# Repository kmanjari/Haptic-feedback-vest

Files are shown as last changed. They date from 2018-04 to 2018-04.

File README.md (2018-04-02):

# Haptic Feedback Vest for Obstacle Detection

Visit our instructable at http://www.instructables.com/id/Haptic-Feedback-Vest-for-Obstacle-Detection/ to view a description of the system breakdown!

This design utilizes a stereo camera and software (Python and SimpleCV) that parses the user's surroundings into a depth map using a Raspberry Pi platform. This depth map is then used to vibrate the vest at a particular location to signify an obstacle in that location. For example, a vibration in the upper left region of the vest would indicate a hazard in the upper-body/leftward side of the surroundings. We also developed a PCB and integrated the physical piezoelectric hardware into a vest to create a functional and wearable prototype.

Final project for EE285: Embedded Systems Workshop course at Stanford University.

Contributors: Shalini Ranmuthu, Vikram Prasad, Jacqueline Speiser, Steven Lin, Meredith Burkle

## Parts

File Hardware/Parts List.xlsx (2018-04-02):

Part | QTY | Cost Per Unit | Total Cost | Vendor | Link
Shorting Jumper | 10 | 0.77 | 0.77 | Digikey | http://www.digikey.com/product-detail/en/sullins-connector-solutions/SPC02SYAN/S9001-ND/76375
Heat Shrink Tubing 1/16" | 1 | 1.15 | 1.15 | Digikey | http://www.digikey.com/product-detail/en/alpha-wire/F221B1-16-BK100/A116B-4-ND/281667
Heat Shrink Tubing 3/32" | 1 | 1.22 | 1.22 | Digikey | http://www.digikey.com/product-detail/en/alpha-wire/F221B3-32-BK100/A332B-4-ND/281669
Fanny Pack | 1 | $15.99 | 15.99 | Amazon | https://www.amazon.com/SoJourner-Bags-Outer-Galaxy-Festival/dp/B01G4A9H9E
Adafruit Vibration Motor | 15 | 1.95 | 29.25 | Digikey | http://www.digikey.com/product-detail/en/adafruit-industries-llc/1201/1528-1177-ND/5353637
2n7002 Nmos | 30 | 0.131 | 3.93 | Digikey | http://www.digikey.com/product-detail/en/on-semiconductor/2N7002LT1G/2N7002LT1GOSCT-ND/917791
10K resistor(0805) | 50 | 0.0092 | 0.46 | Digikey | http://www.digikey.com/product-detail/en/stackpole-electronics-inc/RMCF0805JT10K0/RMCF0805JT10K0CT-ND/1942577
100nF capacitor (0805) | 10 | 0.037 | 0.37 | Digikey | http://www.digikey.com/product-detail/en/avx-corporation/08055C104KAT2A/478-1395-1-ND/564427
1K resistor (0805) | 10 | 0.018 | 0.18 | Digikey | http://www.digikey.com/product-detail/en/yageo/RC0805JR-071KL/311-1.0KARCT-ND/731165
PCA9685 (i2c->PWM controller) | 3 | 2.43 | 7.29 | Digkey | http://www.digikey.com/product-detail/en/nxp-semiconductors/PCA9685PW-Q900,118/568-5931-1-ND/2531218
Surface Mount Diode | 25 | 0.1084 | 2.71 | Digikey | http://www.digikey.com/product-detail/en/smc-diode-solutions/1N4148WTR/1655-1360-1-ND/6022805
Dual Breakaway Header | 3 | 0.93 | 2.79 | Digikey | http://www.digikey.com/product-detail/en/sullins-connector-solutions/PRPC020DAAN-RC/S2011EC-20-ND/2775274
1uF capacitor (TH, Electrolytic) | 3 | 0.11 | 0.33 | Digikey | http://www.digikey.com/product-detail/en/wurth-electronics-inc/860020672005/732-8851-1-ND/5728796
USB B receptacle | 2 | 0.5 | 1 | Digikey | http://www.digikey.com/product-detail/en/pulse-electronics-corporation/E8144-B02022-L/553-2272-ND/4868942
Connector (PCB to piezoelectrics) | 1 | 10.8 | 10.8 | Digikey | http://www.digikey.com/product-detail/en/3m/M1DXA-3440K/M1DXA-3440K-ND/46368
Battery Bank | 1 | $40.00 | 40 | Amazon | https://www.amazon.com/Anker-PowerCore-20100-Capacity-Technology/dp/B00X5RV14Y
GPIO Ribbon Cable | 1 | $2.95 | 2.95 | Adafruit | https://www.adafruit.com/product/1988
Logitech Webcam C310 | 2 | $29.99 | 59.98 | Amazon | https://www.amazon.com/Logitech-960-000585-HD-Webcam-C310/dp/B003LVZO8S?s=electronics
Raspberry Pi | 2 | $35 | $70 | MCM Electronics | http://www.mcmelectronics.com/product/83-17300?COM=superwidget-link_RaspberryPi+CMPNULL
Raspberry Pi Power Supply (for development) | 2 | $8.99 | $17.98 | MCM Electronics | http://www.mcmelectronics.com/product/28-21442
Micro SD cards | 2 | In-house | 0
Vest of wearer's choice |  |  |  | IKEA
USB-B to USB Cable

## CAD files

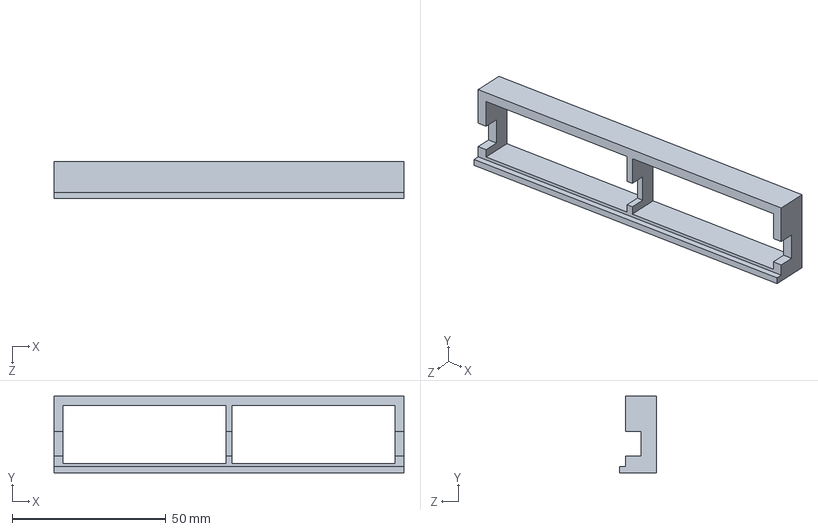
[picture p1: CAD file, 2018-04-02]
Hardware/Haptic Board V1 Gerbers/holder.SLDPRT
114.0 x 25.0 x 12.0 mm

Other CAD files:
Hardware/Haptic Board V1 Gerbers/holder.STL

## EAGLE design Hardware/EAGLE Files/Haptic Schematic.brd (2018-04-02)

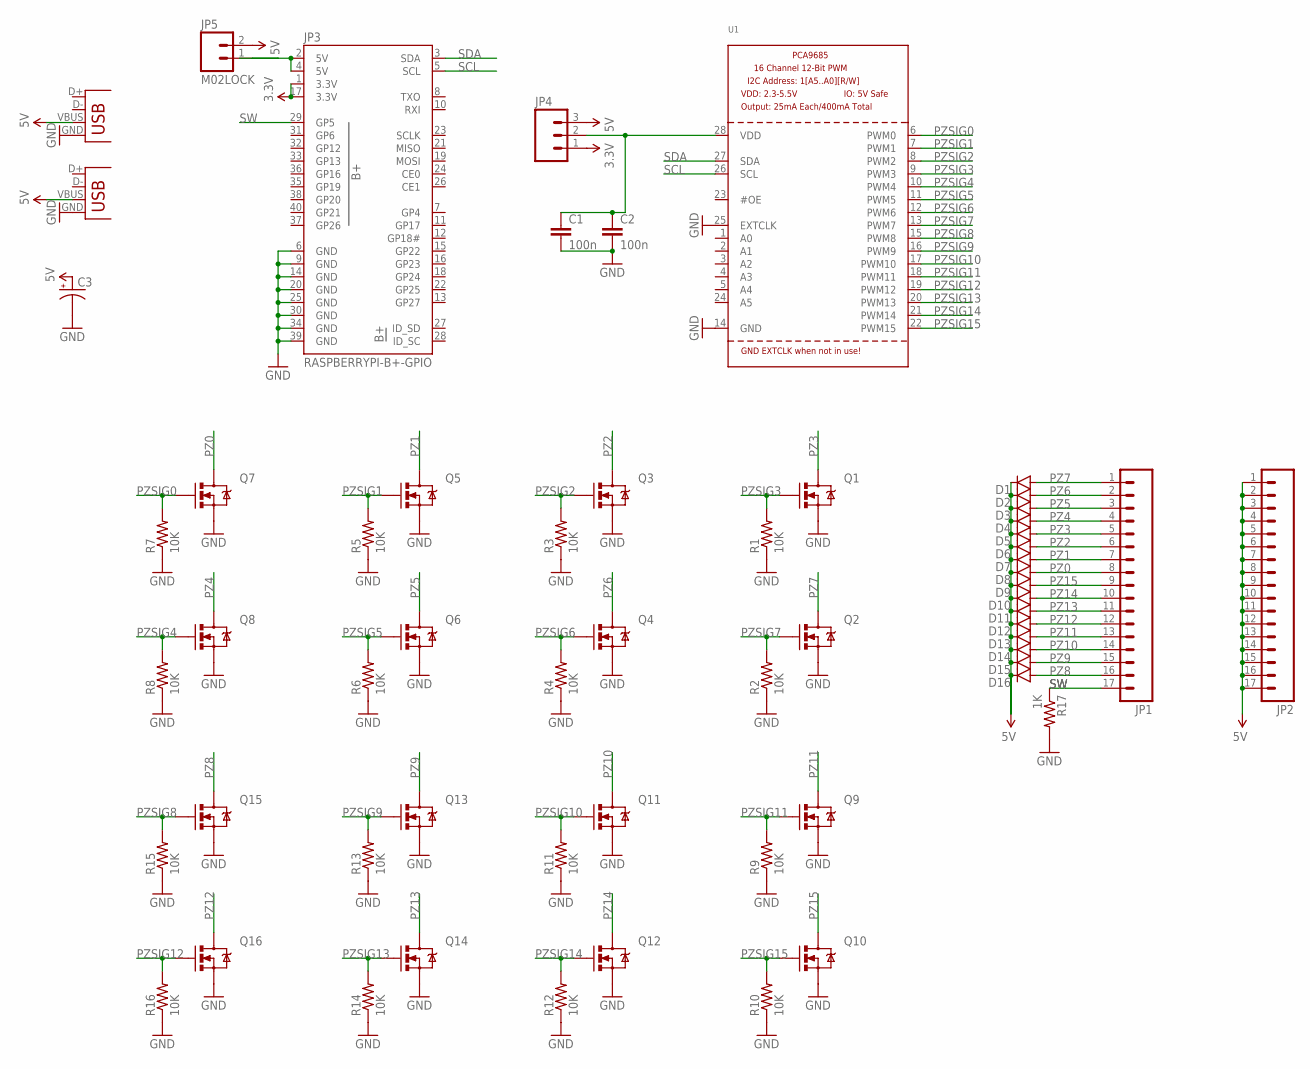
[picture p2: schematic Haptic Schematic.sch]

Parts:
C1, C2: 100n; 0805
C3: CAP_POLPTH2; CPOL-RADIAL-10UF-25V
D1, D2, D3, D4, D5, D6, D7, D8, D9, D10, D11, D12, D13, D14, D15, D16: DIODESOD523; SOD523
JP1, JP2: M17; 1X17
JP3: RASPBERRYPI-B+-GPIO; 2X20-SHROUDED
JP4: M03LOCK; 1X03_LOCK
JP5: M02LOCK; 1X02_LOCK
JP6, JP7: USB-B; USB-B-PTH
Q1, Q2, Q3, Q4, Q5, Q6, Q7, Q8, Q9, Q10, Q11, Q12, Q13, Q14, Q15, Q16: MOSFET-NCHANNEL2N7002PW; SOT323
R1, R2, R3, R4, R5, R6, R7, R8, R9, R10, R11, R12, R13, R14, R15, R16: 10K; 0805
R17: 1K; 0805
U1: PCA9685; TSSOP28

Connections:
3.3V: JP3.1 (3.3V), JP3.17 (3.3V), JP4.1
5V: C3.1 (+), D1.C, D2.C, D3.C, D4.C, D5.C, D6.C, D7.C, D8.C, D9.C, D10.C, D11.C, D12.C, D13.C, D14.C, D15.C, D16.C, JP2.1, JP2.2, JP2.3, JP2.4, JP2.5, JP2.6, JP2.7, JP2.8, JP2.9, JP2.10, JP2.11, JP2.12, JP2.13, JP2.14, JP2.15, JP2.16, JP2.17, JP4.3, JP5.2, JP6.VBUS, JP7.VBUS
GND: C1.2, C2.2, C3.2 (-), JP3.6 (GND), JP3.9 (GND), JP3.14 (GND), JP3.20 (GND), JP3.25 (GND), JP3.30 (GND), JP3.34 (GND), JP3.39 (GND), JP6.GND, JP7.GND, Q1.2 (S), Q2.2 (S), Q3.2 (S), Q4.2 (S), Q5.2 (S), Q6.2 (S), Q7.2 (S), Q8.2 (S), Q9.2 (S), Q10.2 (S), Q11.2 (S), Q12.2 (S), Q13.2 (S), Q14.2 (S), Q15.2 (S), Q16.2 (S), R1.1, R2.1, R3.1, R4.1, R5.1, R6.1, R7.1, R8.1, R9.1, R10.1, R11.1, R12.1, R13.1, R14.1, R15.1, R16.1, R17.2, U1.14 (GND), U1.25 (EXTCLK)
unnamed: JP3.2 (5V), JP3.4 (5V), JP5.1
unnamed: C1.1, C2.1, JP4.2, U1.28 (VDD)
PZ0: D8.A, JP1.8, Q7.3 (D)
PZ1: D7.A, JP1.7, Q5.3 (D)
PZ2: D6.A, JP1.6, Q3.3 (D)
PZ3: D5.A, JP1.5, Q1.3 (D)
PZ4: D4.A, JP1.4, Q8.3 (D)
PZ5: D3.A, JP1.3, Q6.3 (D)
PZ6: D2.A, JP1.2, Q4.3 (D)
PZ7: D1.A, JP1.1, Q2.3 (D)
PZ8: D16.A, JP1.16, Q15.3 (D)
PZ9: D15.A, JP1.15, Q13.3 (D)
PZ10: D14.A, JP1.14, Q11.3 (D)
PZ11: D13.A, JP1.13, Q9.3 (D)
PZ12: D12.A, JP1.12, Q16.3 (D)
PZ13: D11.A, JP1.11, Q14.3 (D)
PZ14: D10.A, JP1.10, Q12.3 (D)
PZ15: D9.A, JP1.9, Q10.3 (D)
PZSIG0: Q7.1 (G), R7.2, U1.6 (PWM0)
PZSIG1: Q5.1 (G), R5.2, U1.7 (PWM1)
PZSIG2: Q3.1 (G), R3.2, U1.8 (PWM2)
PZSIG3: Q1.1 (G), R1.2, U1.9 (PWM3)
PZSIG4: Q8.1 (G), R8.2, U1.10 (PWM4)
PZSIG5: Q6.1 (G), R6.2, U1.11 (PWM5)
PZSIG6: Q4.1 (G), R4.2, U1.12 (PWM6)
PZSIG7: Q2.1 (G), R2.2, U1.13 (PWM7)
PZSIG8: Q15.1 (G), R15.2, U1.15 (PWM8)
PZSIG9: Q13.1 (G), R13.2, U1.16 (PWM9)
PZSIG10: Q11.1 (G), R11.2, U1.17 (PWM10)
PZSIG11: Q9.1 (G), R9.2, U1.18 (PWM11)
PZSIG12: Q16.1 (G), R16.2, U1.19 (PWM12)
PZSIG13: Q14.1 (G), R14.2, U1.20 (PWM13)
PZSIG14: Q12.1 (G), R12.2, U1.21 (PWM14)
PZSIG15: Q10.1 (G), R10.2, U1.22 (PWM15)
SCL: JP3.5 (SCL), U1.26 (SCL)
SDA: JP3.3 (SDA), U1.27 (SDA)
SW: JP1.17, JP3.29 (GP5), R17.1

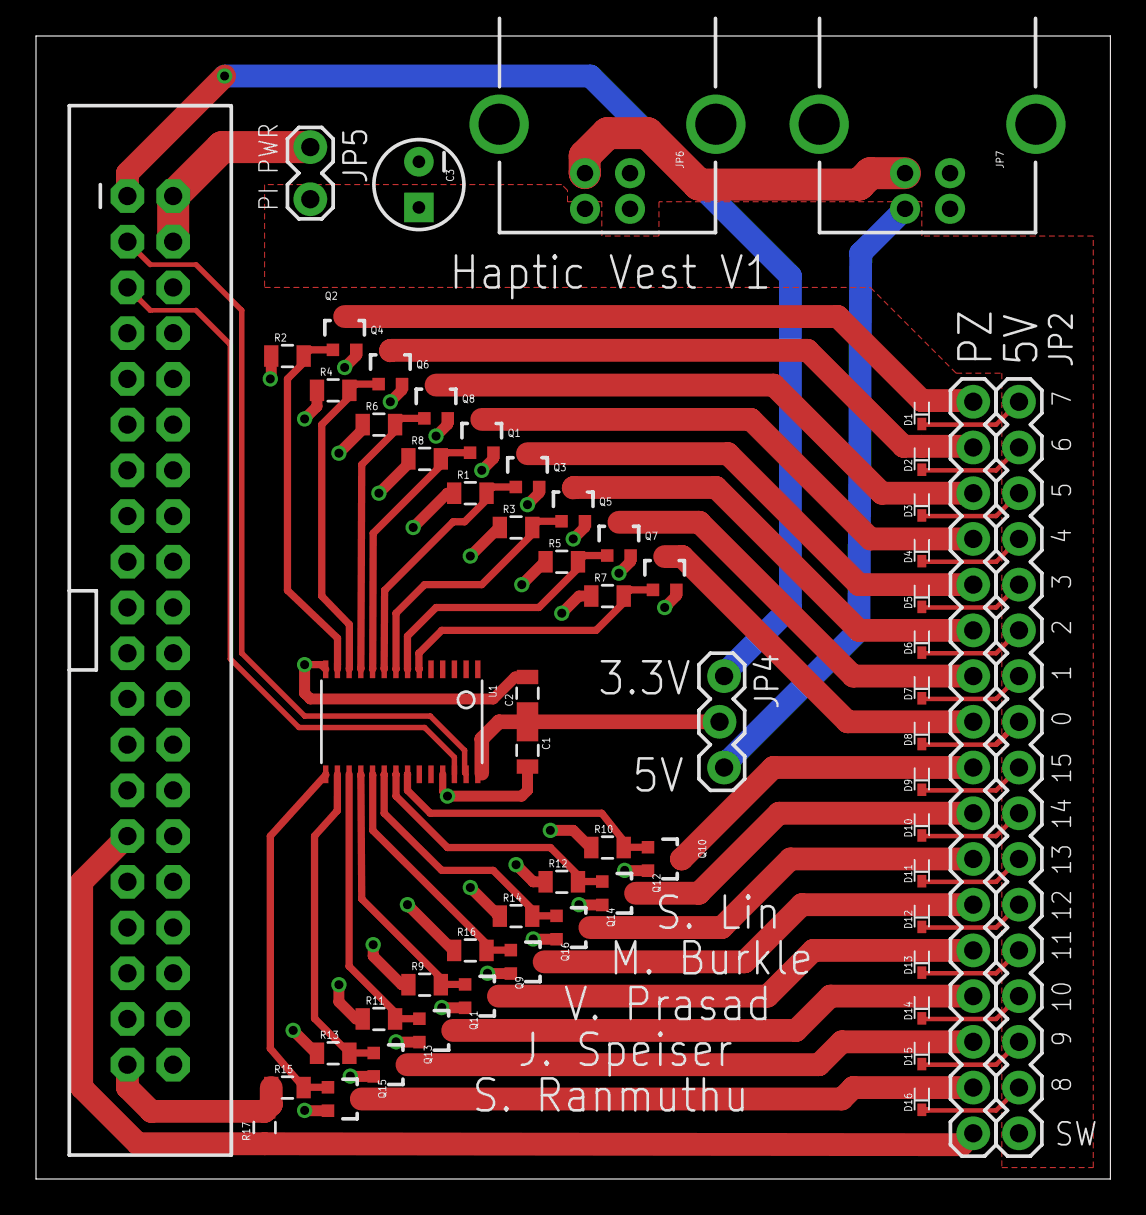
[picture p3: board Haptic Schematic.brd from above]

Board: 2 copper layers, 59.7 x 63.5 mm, 60 parts (0 on the bottom side), 40 nets.

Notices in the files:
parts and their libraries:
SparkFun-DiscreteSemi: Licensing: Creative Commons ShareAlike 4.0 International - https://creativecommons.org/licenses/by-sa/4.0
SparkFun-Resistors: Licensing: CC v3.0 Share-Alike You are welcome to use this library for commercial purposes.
